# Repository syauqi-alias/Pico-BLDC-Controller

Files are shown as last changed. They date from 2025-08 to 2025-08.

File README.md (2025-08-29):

# Pico-BLDC-Controller



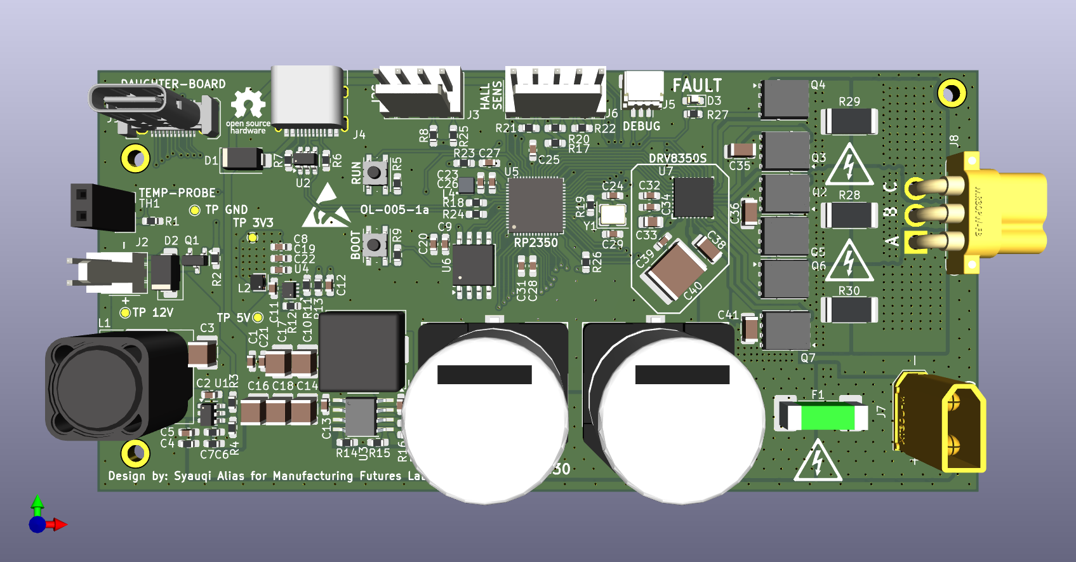
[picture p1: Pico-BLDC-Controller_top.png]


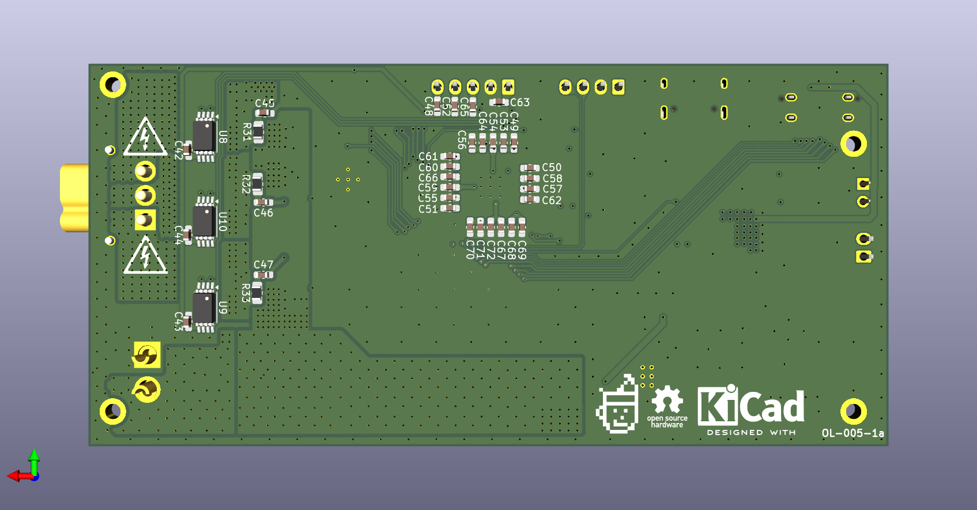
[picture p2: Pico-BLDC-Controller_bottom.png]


This project documents the design of a custom Brushless DC (BLDC) motor controller for a hotplate magnetic stirrer, intended for integration with an Opentrons automated liquid handling robot at the Manufacturing Future Lab, University College London.

---

## Project Overview

The primary goal is to create an open-source, accessible, and robust controller for a **260W 30V/7A Maxon BLDC motor**. This is my first venture into designing a motor controller, especially one involving a three-phase half-bridge topology. The journey is as much about learning as it is about the final product.

---

## Hardware Design

The schematic design is functionally complete and is currently undergoing peer review. The component selection process prioritized simplicity and a reduced component count to make the design easier to understand and replicate.

### Key Components:

* **Microcontroller:** **Raspberry Pi RP2350**
    * Chosen for its straightforward development environment and strong community support. While the ADC conversion speed can be a limitation for high-performance Field-Oriented Control (FOC), the goal is to create a baseline design that the open-source community can build upon and optimize.

* **Pre-driver:** **Texas Instruments DRV8350S**
    * This integrated gate driver significantly simplifies the design by handling much of the complexity associated with driving MOSFETs, such as the need for external charge pumps or bootstrap components. It reduces the overall component count and circuit complexity.

* **Motor:** **Maxon EC 90 flat Ø90 mm, brushless, 260 W, with Hall sensors**
    * A powerful 260W brushless motor, providing more than enough torque for stirring viscous solutions.

---

## Software and Firmware

The initial firmware will be developed using the **[simpleFOC](https://simplefoc.com/)** library to accelerate development and establish a functional baseline.

Once the hardware is validated, a longer-term goal is to develop custom firmware from scratch to fully optimize the controller's performance for this specific application.

---

## Current Status

**Status:** In Development (Last Updated: 29/08/2025)

* [x] Component selection finalized.
* [x] Initial schematic design complete.
* [x] Schematic peer review in progress.
* [x] PCB layout design.
* [X] PCB peer review 
* [X] Send out PCB to manufacturer
* [ ] Prototyping and hardware testing.
* [ ] Firmware development.

I'm actively seeking feedback on the schematic from colleagues and online forums. The design has evolved significantly through this iterative process, and I'll continue to post updates as the project progresses.

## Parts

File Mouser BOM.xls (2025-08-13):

Mfr Part Number (Input) | Manufacturer Part Number | Mouser Part Number | Manufacturer Name | Description | Quantity 1 | Unit Price 1 | Quantity 2 | Unit Price 2 | Quantity 3 | Unit Price 3 | Quantity 4 | Unit Price 4 | Quantity 5 | Unit Price 5 | Order Quantity | Order Unit Price | Min./Mult. | Availability | Lead Time in Days | Lifecycle | NCNR | RoHS | Pb Free | Package Type | Datasheet URL | Product Image | Design Risk
C0603C104K5RACAUTO |  | 80-C0603C104K5RAUTO |  | 100nF | 19
GRM32ER61C476KE15L |  | 81-GRM32ER61C476KE5L |  | 47uF | 3
GRM188D72A105KE01J |  | 81-GRM188D72A105KE1J |  | 1uF | 3
HMK107B7104KAHT |  | 963-HMK107B7104KAHT |  | 0.1uF 100V | 3
KGM15BR50J475KT,MCASL168BD7475KTCA01 |  |  |  | 4.7uF | 6
KGM15ACG1H121JT |  |  |  | 120pF | 1
HMK325B7225KN-T |  |  |  | 2.2uF | 2
KAM32LR72A475KU |  |  |  | 4.7uF | 1
GRM188R60J226MEA0D |  |  |  | 22uF | 2
0603YC101KAT2A,C0402C101K3RACAUTO |  |  |  | 100pF | 12
06033A150JAT2A |  |  |  | 15p | 2
EEV-FK2A331M |  |  |  | 330uF 100V | 2
GXT188R71C105KE13D |  |  |  | 1uF 16V | 2
C2012X7R2A473K125AA |  |  |  | 0.047uF | 1
CL31B105KCHNNNE |  |  |  | 1uF 100V | 4
CGA9N3X7S2A106K230KE |  |  |  | 10uF 100V | 1
 |  |  |  | C | 3
06033A100KAT2A |  |  |  | 10pF | 3
GCM188R71H103KA37J |  |  |  | 0.01uF | 2
SS12 |  |  |  | SS12 | 1
SS14 |  |  |  | SS14 | 1
 |  |  |  | LED | 1
0463030.ER |  |  |  | Fuse | 1
 |  |  |  | MountingHole | 4
 |  |  |  | Conn_01x10 | 1
217796-1021 |  |  |  | Heat Mat | 1
2042-11-22 |  |  |  | I2C CONN | 1
TYPE-C-31-M-12 |  |  |  | USB_C_Receptacle_USB2.0_14P | 1
SM03B-SRSS-TB(LF)(SN) |  |  |  | SM03B-SRSS-TB | 1
22-11-2052 |  |  |  | Conn_01x05 | 1
XT30U-M |  |  |  | Conn_01x02 | 1
MR30PW-F20.G.Y |  |  |  | Conn_01x03 | 1
MSS1210-153MED |  |  |  | 15uH | 1
74479275147 |  |  |  | 470nH | 1
MSS1038-153MLB |  |  |  | 15uH | 1
AOTA-B201610S3R3-101-T |  |  |  | 3.3uH | 1
DMN3053L-7 |  |  |  | DMN3053L-7 | 1
SIR680LDP |  |  |  | SIR680LDP | 6
AC0603JR-7W10KL,CRCW060310K0FKEI |  |  |  | 10k | 4
ERJ-3EKF4223V |  |  |  | 422k | 1
CRCW060322K1FKEBC |  |  |  | 22.1k | 1
RC0603FR-101KL |  |  |  | 1k | 7
CR0603-FX-5101ELF |  |  |  | 5.1k | 2
RC0603FR-7W4K7L |  |  |  | 4.7k | 2
CRCW0603100KFKEA |  |  |  | 100k | 2
ERJ-PB3B1003V |  |  |  | 100k | 1
CR0603-FX-4533ELF |  |  |  | 453k | 1
CRCW060364K9FKEA |  |  |  | 64.9k | 1
CR0603-FX-4022ELF |  |  |  | 40.2k | 1
CR0603-JW-270ELF |  |  |  | 27 | 2
AC0603DR-0733RL |  |  |  | 33 | 1
CRCW0603330RFKEC |  |  |  | 330 | 1
WSLP25122L000FEA |  |  |  | 2m | 3
 |  |  |  | R | 3
434133025816 |  |  |  | SW_Push | 2
B57560G1104F000 |  |  |  | 100k 200 C | 1
 |  |  |  | TestPoint | 4
LMR51430YFDDCR |  |  |  | LMR51430 | 1
82400102 |  |  |  | WE-TVS-82400102 | 1
LMR38020SDDAR |  |  |  | LMR38020SDDAR | 1
TPS62822DLCR |  |  |  | TPS62822DLC | 1
SC1509(13) |  |  |  | RP2350_60QFN | 1
W25Q128JVSIM TR |  |  |  | W25Q128JVS | 1
DRV8350SRTVT |  |  |  | DRV8350S | 1
INA240A2PWR |  |  |  | INA240A2PW | 3
ABM8-272-T3 |  |  |  | ABM8-272-T3 | 1

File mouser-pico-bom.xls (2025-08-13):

Mfr Part Number (Input) | Manufacturer Part Number | Mouser Part Number | Manufacturer Name | Description | Quantity 1 | Unit Price 1 | Quantity 2 | Unit Price 2 | Quantity 3 | Unit Price 3 | Quantity 4 | Unit Price 4 | Quantity 5 | Unit Price 5 | Order Quantity | Order Unit Price | Min./Mult. | Availability | Lead Time in Days | Lifecycle | NCNR | RoHS | Pb Free | Package Type | Datasheet URL | Product Image | Design Risk
80-C0603C104K5RAUTO |  |  |  |  | 19
81-GRM32ER61C476KE5L |  |  |  |  | 3
81-GRM188D72A105KE1J |  |  |  |  | 3
963-HMK107B7104KAHT |  |  |  |  | 3
963-MCASL168BD7475KT |  |  |  |  | 5
581-KGM15ACG1H121JT |  |  |  |  | 1
963-HMK325B7225KN-T |  |  |  |  | 2
581-KAM32LR72A475KU |  |  |  |  | 1
81-GRM188R60J226ME0D |  |  |  |  | 2
581-0603YC101KAT2A |  |  |  |  | 11
581-0603YC101KAT2A |  |  |  |  | 1
581-06033A150JAT2A |  |  |  |  | 2
667-EEV-FK2A331M |  |  |  |  | 2
81-GXT188R71C105KE3D |  |  |  |  | 2
810-C2012X7R2A473K |  |  |  |  | 1
187-CL31B105KCHNNNE |  |  |  |  | 4
810-CGA9N3X7S2A106KS |  |  |  |  | 1
581-06033A100K |  |  |  |  | 3
581-KGM15BR50J475KT |  |  |  |  | 1
81-GCM188R71H103KA7J |  |  |  |  | 2
821-SS12 |  |  |  |  | 1
821-SS14 |  |  |  |  | 1
720-LSQ976.01-N1Q2-1 |  |  |  |  | 1
576-0463030.ER |  |  |  |  | 1
306-B10BPHDSSLFSNP |  |  |  |  | 1
538-217796-1021 |  |  |  |  | 1
538-22-11-2042 |  |  |  |  | 1
306-SM03BSRSSTBLFSNP |  |  |  |  | 1
538-22-11-2052 |  |  |  |  | 1
994-MSS1210-153MED |  |  |  |  | 1
710-74479275147 |  |  |  |  | 1
994-MSS1038-153MLC |  |  |  |  | 1
815-AB201610S3R3101T |  |  |  |  | 1
637-MMFTN3402 |  |  |  |  | 1
78-SIR680LDP-T1-RE3 |  |  |  |  | 6
603-AC0603JR-7W10KL |  |  |  |  | 3
667-ERJ-3EKF4223V |  |  |  |  | 1
71-CRCW060322K1FKEBC |  |  |  |  | 1
603-RC0603FR-101KL |  |  |  |  | 7
652-CR0603FX-5101ELF |  |  |  |  | 2
603-RC0603FR-7W4K7L |  |  |  |  | 2
71-CRCW0603-100K-E3 |  |  |  |  | 2
667-ERJ-PB3B1003V |  |  |  |  | 1
652-CR0603FX-4533ELF |  |  |  |  | 1
71-CRCW0603-64.9K-E3 |  |  |  |  | 1
71-CRCW060310K0FKEI |  |  |  |  | 1
652-CR0603FX-4022ELF |  |  |  |  | 1
652-CR0603-JW-270ELF |  |  |  |  | 2
603-AC0603DR-0733RL |  |  |  |  | 1
71-CRCW0603330RFKEC |  |  |  |  | 1
71-WSLP25122L000FEA |  |  |  |  | 3
710-434133025816 |  |  |  |  | 2
871-B57560G1104F000 |  |  |  |  | 1
595-LMR51430YFDDCR |  |  |  |  | 1
710-82400102 |  |  |  |  | 1
595-LMR38020SDDAR |  |  |  |  | 1
595-TPS62822DLCR |  |  |  |  | 1
358-SC150913 |  |  |  |  | 1
454-W25Q128JVSIMTR |  |  |  |  | 1
595-DRV8350SRTVT |  |  |  |  | 1
595-INA240A2PWR |  |  |  |  | 3
815-ABM8-272-T3 |  |  |  |  | 1

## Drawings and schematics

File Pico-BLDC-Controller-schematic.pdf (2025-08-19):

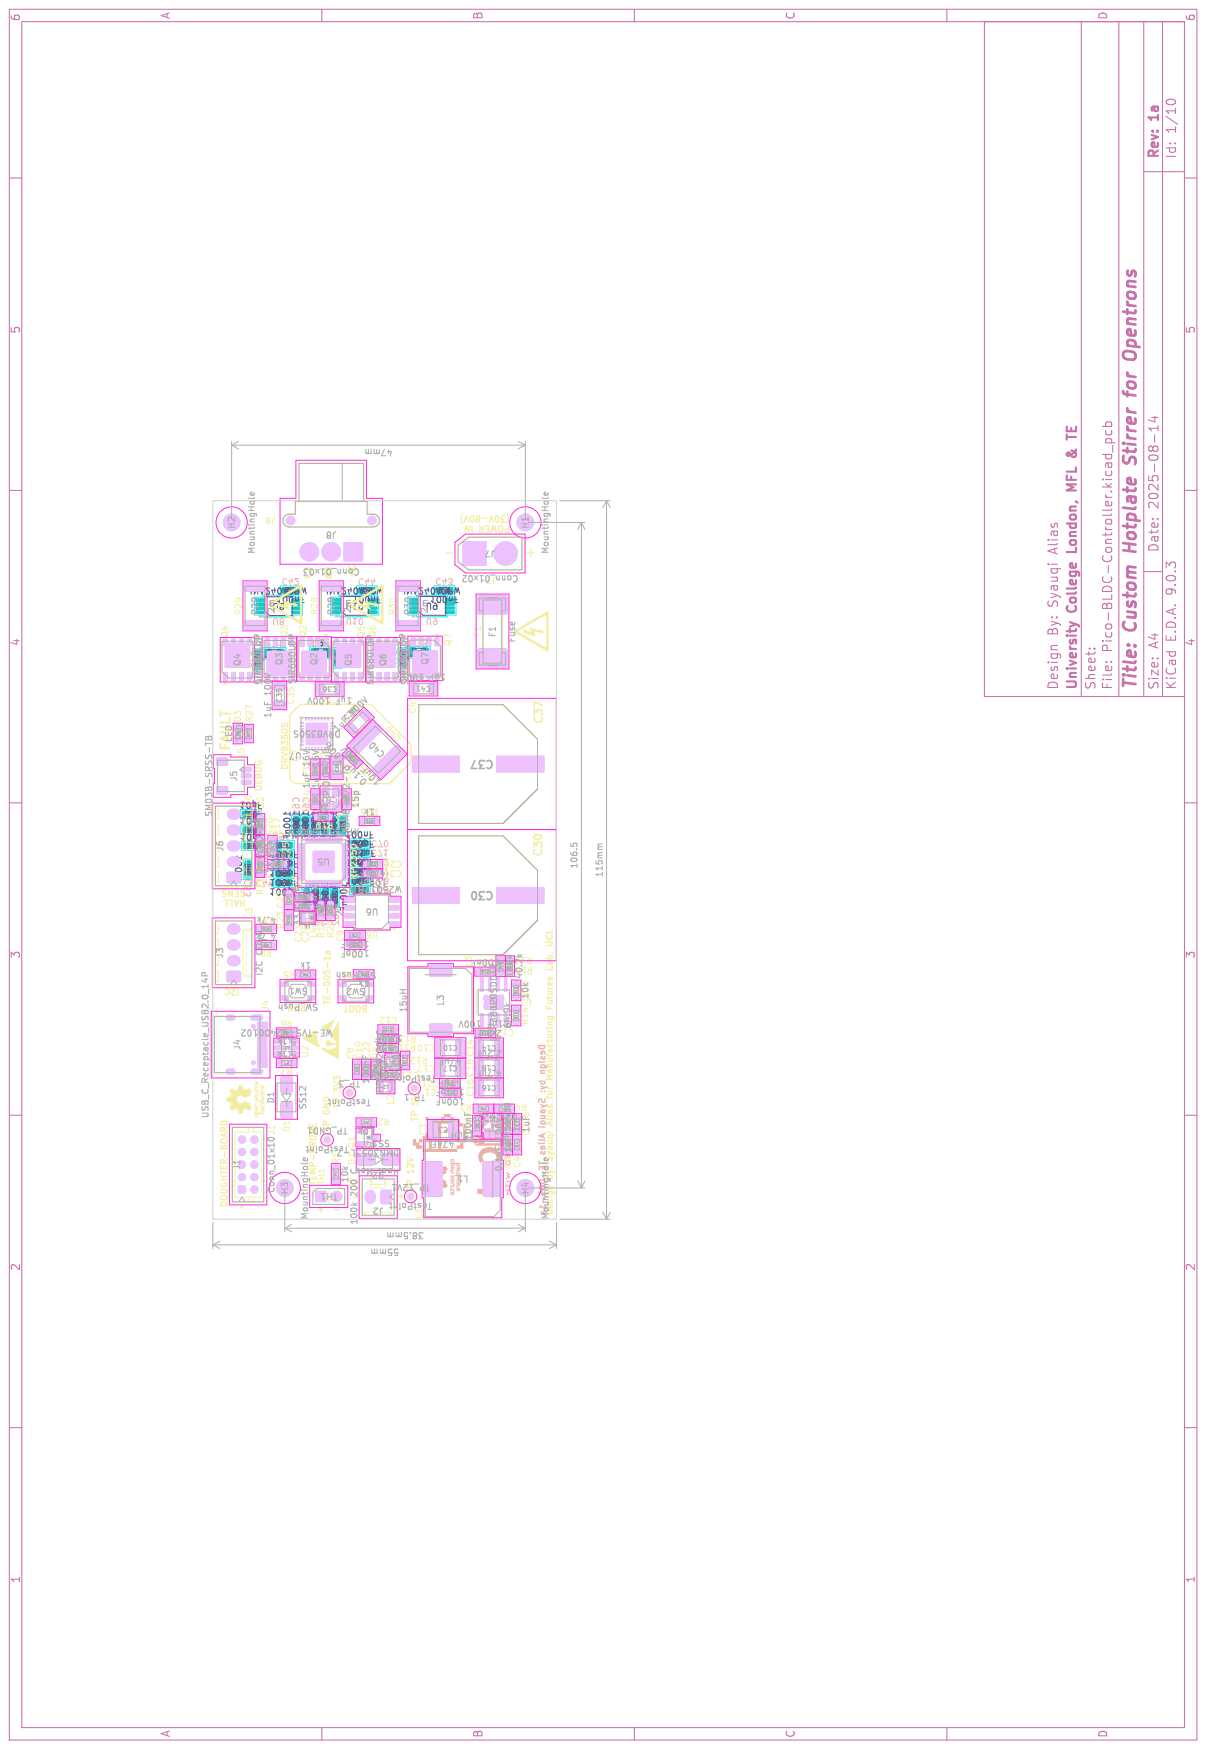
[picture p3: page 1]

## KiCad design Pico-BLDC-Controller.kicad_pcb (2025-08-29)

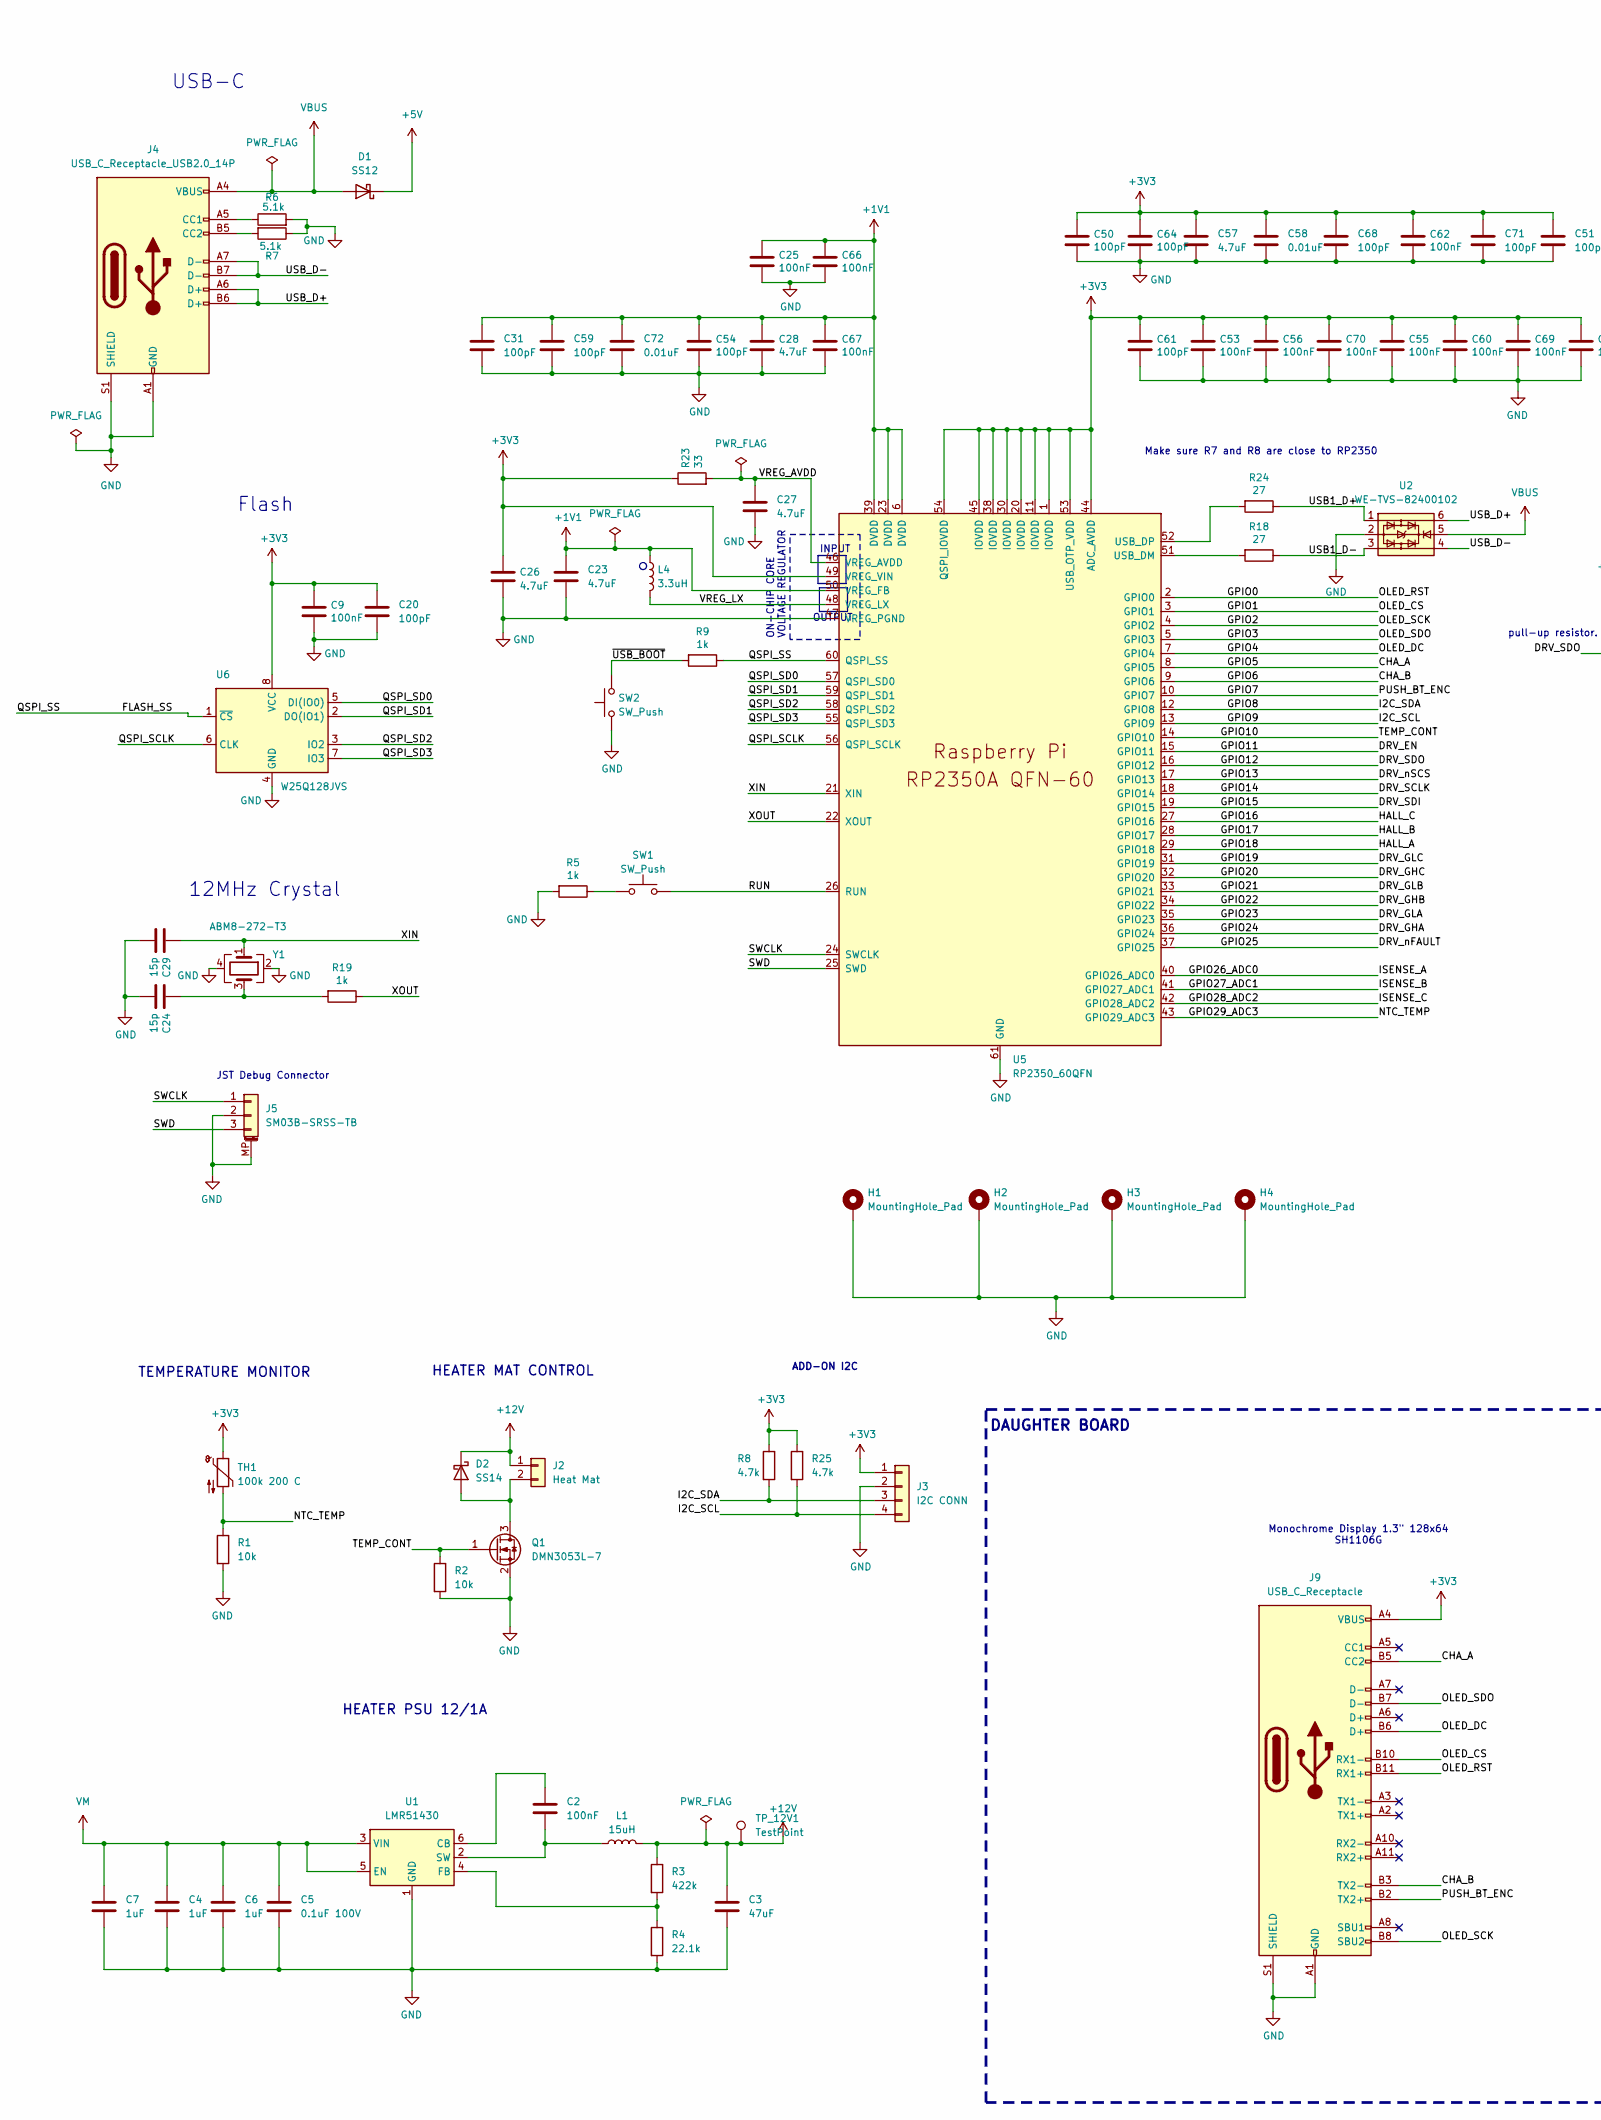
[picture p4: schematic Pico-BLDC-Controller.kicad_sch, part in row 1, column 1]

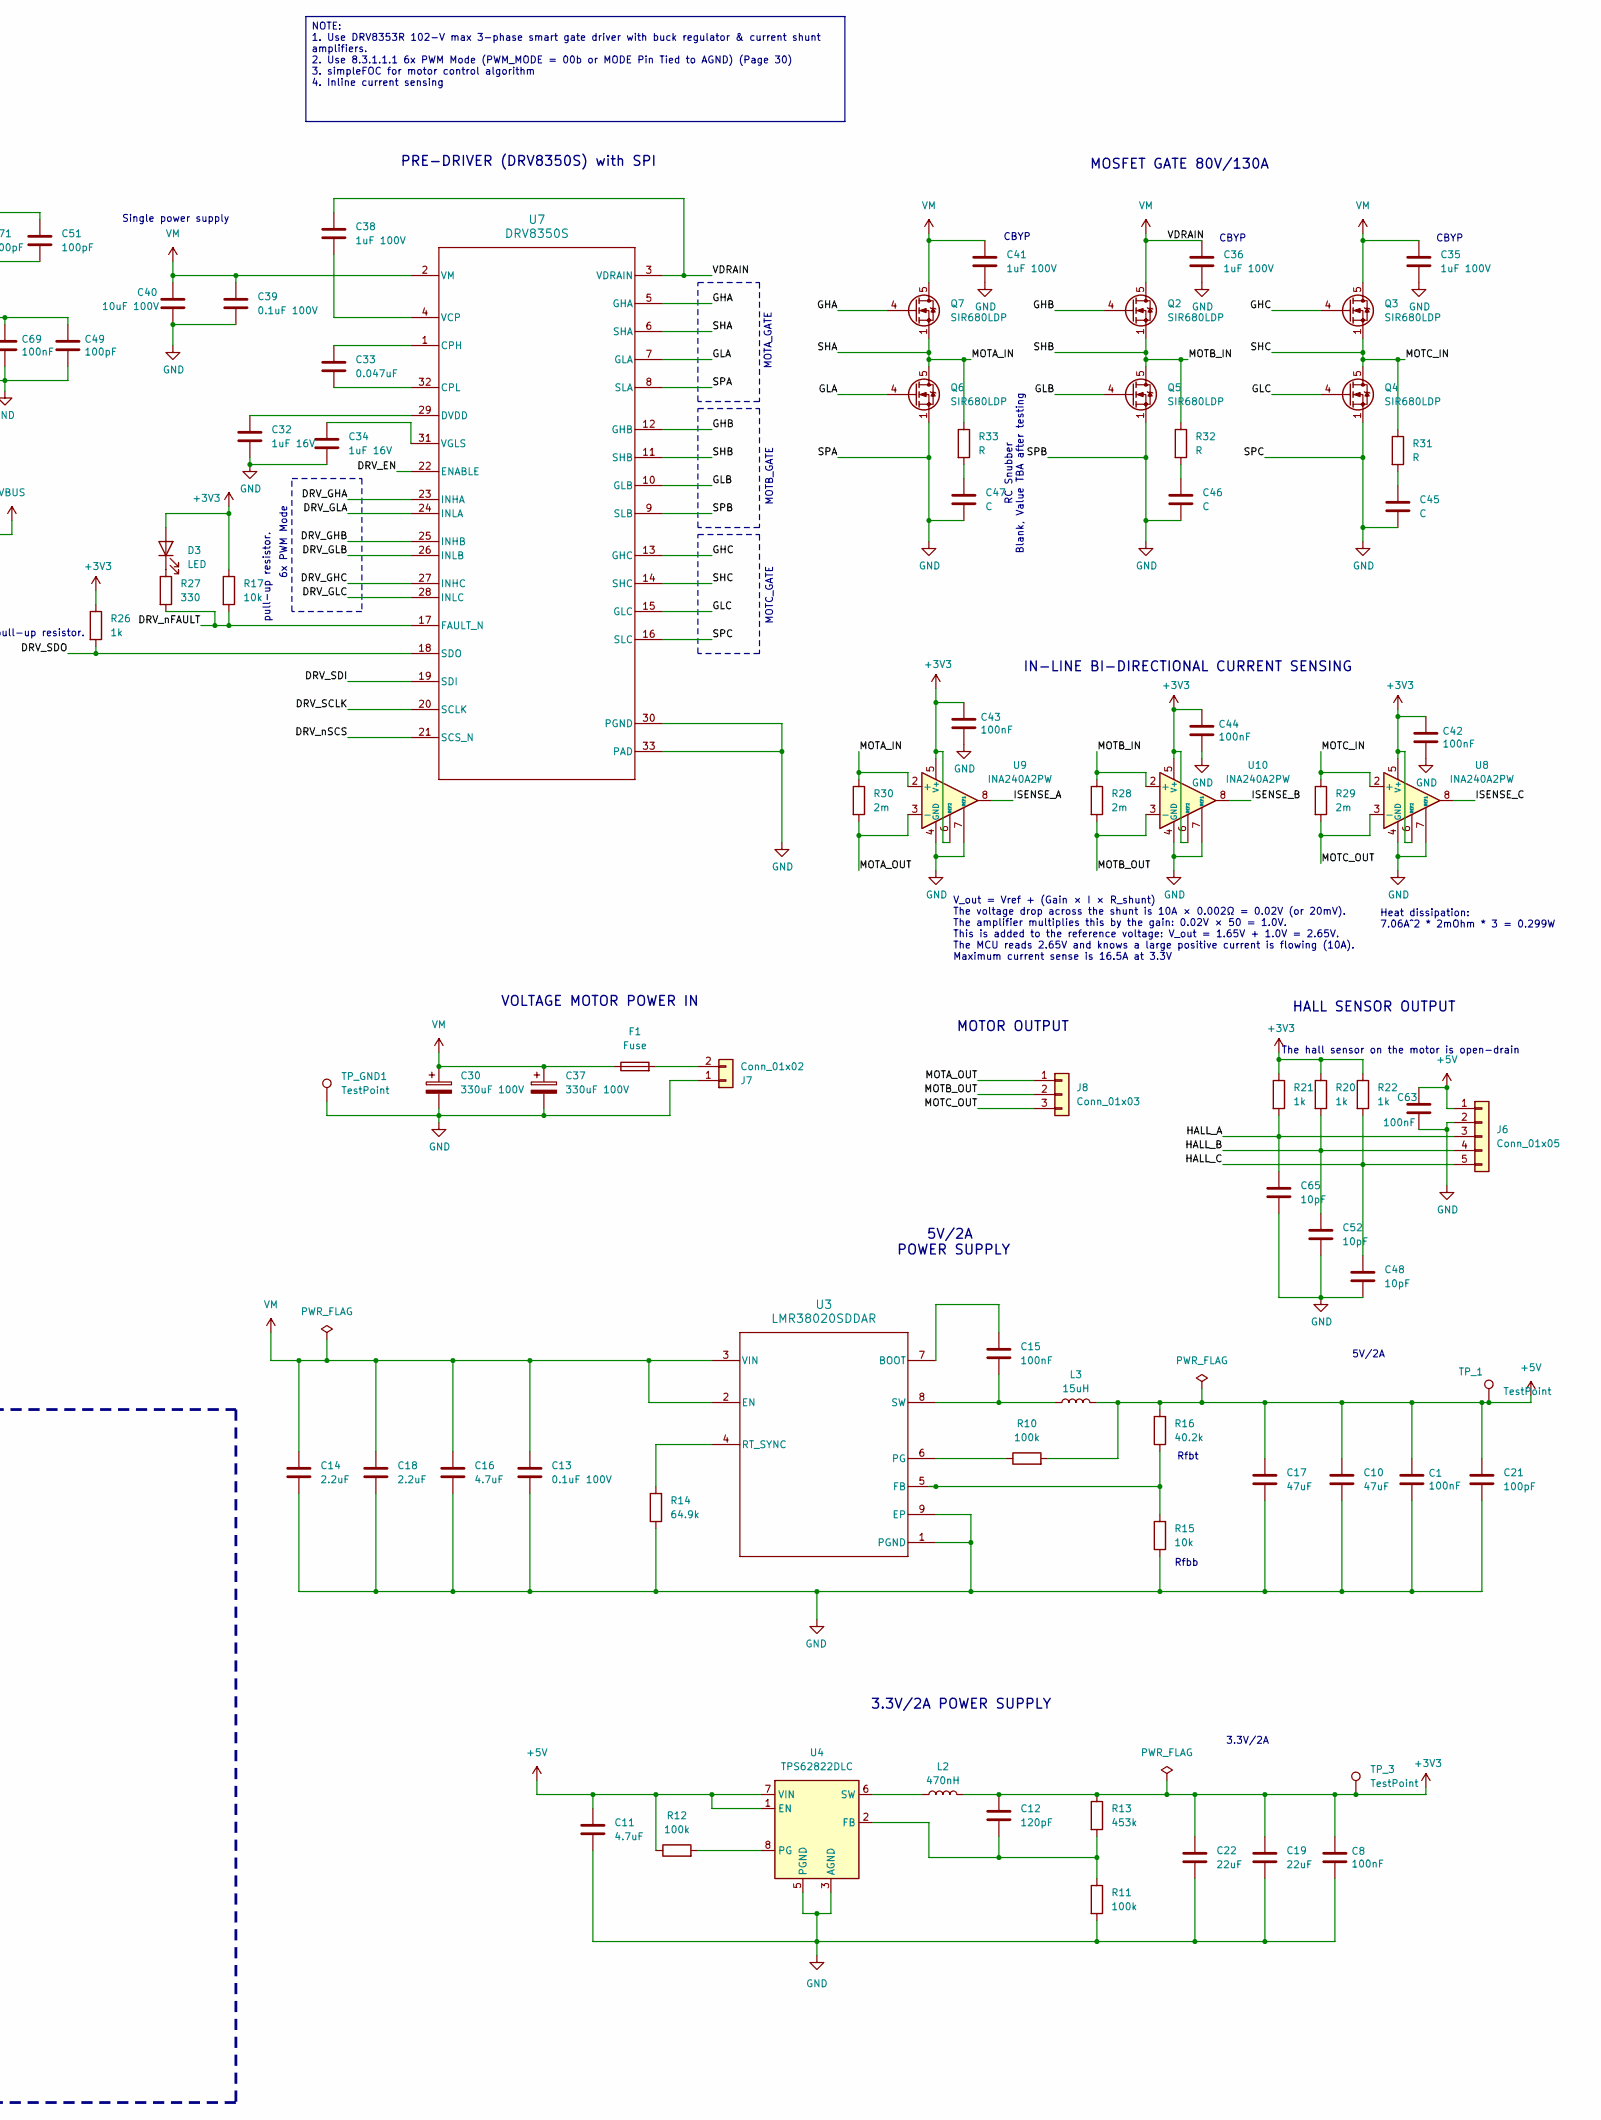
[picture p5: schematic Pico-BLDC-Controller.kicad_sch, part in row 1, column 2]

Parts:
C1, C2, C8, C9, C15, C25, C42, C43, C44, C53, C55, C56, C60, C62, C63, C66, C67, C69, C70: 100nF; C_0603_1608Metric_Pad1.08x0.95mm_HandSolder; MPN C0603C104K5RACAUTO
C3, C10, C17: 47uF; C_1210_3225Metric_Pad1.33x2.70mm_HandSolder; MPN GRM32ER61C476KE15L
C4, C6, C7: 1uF; R_0603_1608Metric_Pad0.98x0.95mm_HandSolder; MPN GRM188D72A105KE01J
C5, C13, C39: 0.1uF 100V; C_0603_1608Metric_Pad1.08x0.95mm_HandSolder; MPN HMK107B7104KAHT
C11, C23, C26, C27, C28: 4.7uF; C_0603_1608Metric_Pad1.08x0.95mm_HandSolder; MPN MCASL168BD7475KTCA01
C12: 120pF; C_0603_1608Metric_Pad1.08x0.95mm_HandSolder; MPN KGM15ACG1H121JT
C14, C18: 2.2uF; C_1210_3225Metric; MPN HMK325B7225KN-T
C16: 4.7uF; C_1210_3225Metric; MPN KAM32LR72A475KU
C19, C22: 22uF; C_0603_1608Metric_Pad1.08x0.95mm_HandSolder; MPN GRM188R60J226MEA0D
C20, C31, C49, C50, C51, C54, C59, C61, C64, C68, C71: 100pF; C_0603_1608Metric_Pad1.08x0.95mm_HandSolder; MPN 0603YC101KAT2A
C21: 100pF; C_0603_1608Metric_Pad1.08x0.95mm_HandSolder; MPN C0402C101K3RACAUTO
C24, C29: 15p; C_0603_1608Metric_Pad1.08x0.95mm_HandSolder; MPN 06033A150JAT2A
C30, C37: 330uF 100V; EEEFK0J103SM; MPN EEV-FK2A331M
C32, C34: 1uF 16V; C_0603_1608Metric_Pad1.08x0.95mm_HandSolder; MPN GXT188R71C105KE13D
C33: 0.047uF; C_0805_2012Metric_Pad1.18x1.45mm_HandSolder; MPN C2012X7R2A473K125AA
C35, C36, C38, C41: 1uF 100V; C_1206_3216Metric; MPN CL31B105KCHNNNE
C40: 10uF 100V; C_2220_5750Metric_Pad1.97x5.40mm_HandSolder; MPN CGA9N3X7S2A106K230KE
C45, C46, C47: C; C_0603_1608Metric_Pad1.08x0.95mm_HandSolder
C48, C52, C65: 10pF; C_0603_1608Metric_Pad1.08x0.95mm_HandSolder; MPN 06033A100KAT2A
C57: 4.7uF; C_0603_1608Metric_Pad1.08x0.95mm_HandSolder; MPN KGM15BR50J475KT
C58, C72: 0.01uF; C_0603_1608Metric_Pad1.08x0.95mm_HandSolder; MPN GCM188R71H103KA37J
D1: SS12; D_SMA; MPN SS12
D2: SS14; D_SMA; MPN SS14
D3: LED; LED_0603_1608Metric_Pad1.05x0.95mm_HandSolder
F1: Fuse; Fuse_Schurter_UMZ250; MPN 0463030.ER
H1, H2, H3, H4: MountingHole_Pad; MountingHole_2.2mm_M2_DIN965_Pad_TopBottom
J2: Heat Mat; Molex_KK-254_AE-6410-02A_1x02_P2.54mm_Vertical; MPN 217796-1021
J3: I2C CONN; Molex_KK-254_AE-6410-04A_1x04_P2.54mm_Vertical; MPN 22-11-2042
J4: USB_C_Receptacle_USB2.0_14P; USB_C_Receptacle_HRO_TYPE-C-31-M-12; MPN TYPE-C-31-M-12
J5: SM03B-SRSS-TB; JST_SH_SM03B-SRSS-TB_1x03-1MP_P1.00mm_Horizontal; MPN SM03B-SRSS-TB(LF)(SN)
J6: Conn_01x05; Molex_KK-254_AE-6410-05A_1x05_P2.54mm_Vertical; MPN 22-11-2052
J7: Conn_01x02; AMASS_XT30U-M_1x02_P5.0mm_Vertical; MPN XT30U-M
J8: Conn_01x03; AMASS_MR30PW-FB_1x03_P3.50mm_Horizontal; MPN MR30PW-F20.G.Y
J9: USB_C_Receptacle; USB_C_Receptacle_JAE_DX07S024WJ3R400
L1: 15uH; L_Coilcraft_MSS1210-XXX; MPN MSS1210-153MED
L2: 470nH; L_Wurth_WE-LQSH-2010; MPN 74479275147
L3: 15uH; L_Coilcraft_MSS1038-XXX; MPN MSS1038-153MLB
L4: 3.3uH; L_pol_2016; MPN AOTA-B201610S3R3-101-T
Q1: DMN3053L-7; SOT-23; MPN DMN3053L-7
Q2, Q3, Q4, Q5, Q6, Q7: SIR680LDP; PowerPAK_SO-8_Single; MPN SIR680LDP
R1, R2, R17: 10k; R_0603_1608Metric_Pad0.98x0.95mm_HandSolder; MPN AC0603JR-7W10KL
R3: 422k; R_0603_1608Metric_Pad0.98x0.95mm_HandSolder; MPN ERJ-3EKF4223V
R4: 22.1k; R_0603_1608Metric_Pad0.98x0.95mm_HandSolder; MPN CRCW060322K1FKEBC
R5, R9, R19, R20, R21, R22, R26: 1k; R_0603_1608Metric_Pad0.98x0.95mm_HandSolder; MPN RC0603FR-101KL
R6, R7: 5.1k; R_0603_1608Metric_Pad0.98x0.95mm_HandSolder; MPN CR0603-FX-5101ELF
R8, R25: 4.7k; R_0603_1608Metric_Pad0.98x0.95mm_HandSolder; MPN RC0603FR-7W4K7L
R10, R11: 100k; R_0603_1608Metric_Pad0.98x0.95mm_HandSolder; MPN CRCW0603100KFKEA
R12: 100k; R_0603_1608Metric; MPN ERJ-PB3B1003V
R13: 453k; R_0603_1608Metric_Pad0.98x0.95mm_HandSolder; MPN CR0603-FX-4533ELF
R14: 64.9k; R_0603_1608Metric_Pad0.98x0.95mm_HandSolder; MPN CRCW060364K9FKEA
R15: 10k; R_0603_1608Metric_Pad0.98x0.95mm_HandSolder; MPN CRCW060310K0FKEI
R16: 40.2k; R_0603_1608Metric_Pad0.98x0.95mm_HandSolder; MPN CR0603-FX-4022ELF
R18, R24: 27; R_0603_1608Metric_Pad0.98x0.95mm_HandSolder; MPN CR0603-JW-270ELF
R23: 33; R_0603_1608Metric_Pad0.98x0.95mm_HandSolder; MPN AC0603DR-0733RL
R27: 330; R_0603_1608Metric; MPN CRCW0603330RFKEC
R28, R29, R30: 2m; R_2512_6332Metric_Pad1.40x3.35mm_HandSolder; MPN WSLP25122L000FEA
R31, R32, R33: R; R_0805_2012Metric_Pad1.20x1.40mm_HandSolder
SW1, SW2: SW_Push; SW_Push_1P1T_NO_Vertical_Wuerth_434133025816; MPN 434133025816
TH1: 100k 200 C; PinSocket_1x02_P2.54mm_Vertical; MPN B57560G1104F000
TP_1, TP_3, TP_12V1: TestPoint; TestPoint_Pad_D1.0mm
TP_GND1: TestPoint; TestPoint_Pad_D1.0mm
U1: LMR51430; SOT-23-6; MPN LMR51430YFDDCR
U2: WE-TVS-82400102; SOT-23-6; MPN 82400102
U3: LMR38020SDDAR; DDA0008E-MFG; MPN LMR38020SDDAR
U4: TPS62822DLC; Texas_VSON-HR-8_1.5x2mm_P0.5mm; MPN TPS62822DLCR
U5: RP2350_60QFN; RP2350-QFN-60-1EP_7x7_P0.4mm_EP3.4x3.4mm_ThermalVias; MPN SC1509(13)
U6: W25Q128JVS; SOIC-8_5.3x5.3mm_P1.27mm; MPN W25Q128JVSIM TR
U7: DRV8350S; RTV0032E; MPN DRV8350SRTVT
U8, U9, U10: INA240A2PW; TSSOP-8_4.4x3mm_P0.65mm; MPN INA240A2PWR
Y1: ABM8-272-T3; Crystal_SMD_3225-4Pin_3.2x2.5mm; MPN ABM8-272-T3

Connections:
+1V1: C23.1, C25.1, C28.1, C31.1, C54.1, C59.1, C66.1, C67.1, C72.1, L4.1, U5.6 (DVDD), U5.23 (DVDD), U5.39 (DVDD), U5.50 (VREG_FB)
+3V3: C8.1, C9.1, C12.1, C19.1, C20.1, C22.1, C26.1, C42.1, C43.1, C44.1, C49.1, C50.1, C51.1, C53.1, C55.1, C56.1, C57.1, C58.1, C60.1, C61.1, C62.1, C64.1, C68.1, C69.1, C70.1, C71.1, D3.2 (A), J3.1, J9.A4 (VBUS), J9.A9 (VBUS), J9.B4 (VBUS), J9.B9 (VBUS), L2.2, R8.1, R13.1, R17.1, R20.1, R21.1, R22.1, R23.1, R25.1, R26.1, TH1.1, TP_3.1, U5.1 (IOVDD), U5.11 (IOVDD), U5.20 (IOVDD), U5.30 (IOVDD), U5.38 (IOVDD), U5.44 (ADC_AVDD), U5.45 (IOVDD), U5.49 (VREG_VIN), U5.53 (USB_OTP_VDD), U5.54 (QSPI_IOVDD), U6.8 (VCC), U8.5 (V+), U8.6 (REF2), U9.5 (V+), U9.6 (REF2), U10.5 (V+), U10.6 (REF2)
+5V: C1.1, C10.1, C11.1, C17.1, C21.1, C63.1, D1.1 (K), J6.1, L3.2, R10.2, R12.1, R16.2, TP_1.1, U4.1 (EN), U4.7 (VIN)
+12V: C3.1, D2.1 (K), J2.1, L1.2, R3.1, TP_12V1.1
/CHA_A: J9.B5 (CC2), U5.8 (GPIO5)
/CHA_B: J9.B3 (TX2-), U5.9 (GPIO6)
/DRV_EN: U5.15 (GPIO11), U7.22 (ENABLE)
/DRV_GHA: U5.36 (GPIO24), U7.23 (INHA)
/DRV_GHB: U5.34 (GPIO22), U7.25 (INHB)
/DRV_GHC: U5.32 (GPIO20), U7.27 (INHC)
/DRV_GLA: U5.35 (GPIO23), U7.24 (INLA)
/DRV_GLB: U5.33 (GPIO21), U7.26 (INLB)
/DRV_GLC: U5.31 (GPIO19), U7.28 (INLC)
/DRV_SCLK: U5.18 (GPIO14), U7.20 (SCLK)
/DRV_SDI: U5.19 (GPIO15), U7.19 (SDI)
/DRV_SDO: R26.2, U5.16 (GPIO12), U7.18 (SDO)
/DRV_nFAULT: R17.2, R27.2, U5.37 (GPIO25), U7.17 (FAULT_N)
/DRV_nSCS: U5.17 (GPIO13), U7.21 (SCS_N)
/FLASH_SS: R9.1, U5.60 (QSPI_SS), U6.1 (~CS)
/GHA: Q7.4 (G), U7.5 (GHA)
/GHB: Q2.4 (G), U7.12 (GHB)
/GHC: Q3.4 (G), U7.13 (GHC)
/GLA: Q6.4 (G), U7.7 (GLA)
/GLB: Q5.4 (G), U7.10 (GLB)
/GLC: Q4.4 (G), U7.15 (GLC)
/GPIO0: J9.B11 (RX1+), U5.2 (GPIO0)
/GPIO1: J9.B10 (RX1-), U5.3 (GPIO1)
/GPIO2: J9.B8 (SBU2), U5.4 (GPIO2)
/GPIO3: J9.B7 (D-), U5.5 (GPIO3)
/GPIO4: J9.B6 (D+), U5.7 (GPIO4)
/GPIO7: J9.B2 (TX2+), U5.10 (GPIO7)
/GPIO8: J3.3, R8.2, U5.12 (GPIO8)
/GPIO9: J3.4, R25.2, U5.13 (GPIO9)
/GPIO10: Q1.1 (G), R2.1, U5.14 (GPIO10)
/GPIO16: C48.1, J6.5, R22.2, U5.27 (GPIO16)
/GPIO17: C52.1, J6.4, R20.2, U5.28 (GPIO17)
/GPIO18: C65.1, J6.3, R21.2, U5.29 (GPIO18)
/GPIO26_ADC0: U5.40 (GPIO26_ADC0), U9.8
/GPIO27_ADC1: U5.41 (GPIO27_ADC1), U10.8
/GPIO28_ADC2: U5.42 (GPIO28_ADC2), U8.8
/GPIO29_ADC3: R1.1, TH1.2, U5.43 (GPIO29_ADC3)
/MOTA_IN: Q6.5 (D), Q7.1 (S), Q7.2 (S), Q7.3 (S), R30.1, R33.1, U7.6 (SHA), U9.2 (+)
/MOTA_OUT: J8.1, R30.2, U9.3 (-)
/MOTB_IN: Q2.1 (S), Q2.2 (S), Q2.3 (S), Q5.5 (D), R28.1, R32.1, U7.11 (SHB), U10.2 (+)
/MOTB_OUT: J8.2, R28.2, U10.3 (-)
/MOTC_IN: Q3.1 (S), Q3.2 (S), Q3.3 (S), Q4.5 (D), R29.1, R31.1, U7.14 (SHC), U8.2 (+)
/MOTC_OUT: J8.3, R29.2, U8.3 (-)
/QSPI_SCLK: U5.56 (QSPI_SCLK), U6.6 (CLK)
/QSPI_SD0: U5.57 (QSPI_SD0), U6.5 (DI(IO0))
/QSPI_SD1: U5.59 (QSPI_SD1), U6.2 (DO(IO1))
/QSPI_SD2: U5.58 (QSPI_SD2), U6.3 (IO2)
/QSPI_SD3: U5.55 (QSPI_SD3), U6.7 (IO3)
/RUN: SW1.2, U5.26 (RUN)
/SWCLK: J5.1, U5.24 (SWCLK)
/SWD: J5.3, U5.25 (SWD)
/USB1_D+: R24.1, U2.1
/USB1_D-: R18.1, U2.3
/USB_D+: J4.A6 (D+), J4.B6 (D+), U2.6
/USB_D-: J4.A7 (D-), J4.B7 (D-), U2.4
/VREG_AVDD: C27.1, R23.2, U5.46 (VREG_AVDD)
/VREG_LX: L4.2, U5.48 (VREG_LX)
/XIN: C29.1, U5.21 (XIN), Y1.1
/XOUT: R19.1, U5.22 (XOUT)
/~USB_BOOT: R9.2, SW2.2
GND: C1.2, C3.2, C4.2, C5.2, C6.2, C7.2, C8.2, C9.2, C10.2, C11.2, C13.2, C14.2, C16.2, C17.2, C18.2, C19.2, C20.2, C21.2, C22.2, C23.2, C24.2, C25.2, C26.2, C27.2, C28.2, C29.2, C30.2, C31.2, C32.2, C34.2, C35.2, C36.2, C37.2, C39.2, C40.2, C41.2, C42.2, C43.2, C44.2, C45.2, C46.2, C47.2, C48.2, C49.2, C50.2, C51.2, C52.2, C53.2, C54.2, C55.2, C56.2, C57.2, C58.2, C59.2, C60.2, C61.2, C62.2, C63.2, C64.2, C65.2, C66.2, C67.2, C68.2, C69.2, C70.2, C71.2, C72.2, H1.1, H2.1, H3.1, H4.1, J3.2, J4.A1 (GND), J4.A12 (GND), J4.B1 (GND), J4.B12 (GND), J4.S1 (SHIELD), J5.2, J5.MP (MountPin), J6.2, J7.1, J9.A1 (GND), J9.A12 (GND), J9.B1 (GND), J9.B12 (GND), J9.S1 (SHIELD), Q1.2 (S), Q4.1 (S), Q4.2 (S), Q4.3 (S), Q5.1 (S), Q5.2 (S), Q5.3 (S), Q6.1 (S), Q6.2 (S), Q6.3 (S), R1.2, R2.2, R4.2, R5.2, R6.2, R7.1, R11.2, R14.1, R15.1, SW2.1, TP_GND1.1, U1.1 (GND), U2.2, U3.1 (PGND), U3.9 (EP), U3.10, U3.11, U3.12, U3.13, U3.14, U3.15, U4.3 (AGND), U4.5 (PGND), U5.47 (VREG_PGND), U5.61 (GND), U6.4 (GND), U7.8 (SLA), U7.9 (SLB), U7.16 (SLC), U7.30 (PGND), U7.33 (PAD), U8.1 (GND), U8.4 (GND), U8.7 (REF1), U9.1 (GND), U9.4 (GND), U9.7 (REF1), U10.1 (GND), U10.4 (GND), U10.7 (REF1), Y1.2, Y1.4
unnamed: C24.1, R19.2, Y1.3
unnamed: C45.1, R31.2
unnamed: C46.1, R32.2
unnamed: C47.1, R33.2
unnamed: D2.2 (A), J2.2, Q1.3 (D)
unnamed: D3.1 (K), R27.1
unnamed: J4.A5 (CC1), R6.1
unnamed: J4.B5 (CC2), R7.2
unnamed: F1.2, J7.2
unnamed: R5.1, SW1.1
unnamed: C2.1, U1.6 (CB)
unnamed: R3.2, R4.1, U1.4 (FB)
unnamed: C2.2, L1.1, U1.2 (SW)
unnamed: C15.1, U3.7 (BOOT)
unnamed: R15.2, R16.1, U3.5 (FB)
unnamed: R10.1, U3.6 (PG)
unnamed: R14.2, U3.4 (RT_SYNC)
unnamed: C15.2, L3.1, U3.8 (SW)
unnamed: C12.2, R11.1, R13.2, U4.2 (FB)
unnamed: R12.2, U4.8 (PG)
unnamed: L2.1, U4.6 (SW)
unnamed: R18.2, U5.51 (USB_DM)
unnamed: R24.2, U5.52 (USB_DP)
unnamed: C33.1, U7.1 (CPH)
unnamed: C33.2, U7.32 (CPL)
unnamed: C32.1, U7.29 (DVDD)
unnamed: C38.2, U7.4 (VCP)
unnamed: C34.1, U7.31 (VGLS)
VBUS: D1.2 (A), J4.A4 (VBUS), J4.A9 (VBUS), J4.B4 (VBUS), J4.B9 (VBUS), U2.5
VM: C4.1, C5.1, C6.1, C7.1, C13.1, C14.1, C16.1, C18.1, C30.1, C35.1, C36.1, C37.1, C38.1, C39.1, C40.1, C41.1, F1.1, Q2.5 (D), Q3.5 (D), Q7.5 (D), U1.3 (VIN), U1.5 (EN), U3.2 (EN), U3.3 (VIN), U7.2 (VM), U7.3 (VDRAIN)

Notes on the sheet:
CBYP
PRE-DRIVER (DRV8350S) with SPI
3.3V/2A POWER SUPPLY
TEMPERATURE MONITOR
3.3V/2A
Rfbt
Heat dissipation: 7.06A^2 * 2mOhm * 3 = 0.299W
12MHz Crystal
MOTC_GATE
INPUT
MOTOR OUTPUT
Rfbb
Monochrome Display 1.3" 128x64 SH1106G
pull-up resistor.
6x PWM Mode
5V/2A POWER SUPPLY
JST Debug Connector
IN-LINE BI-DIRECTIONAL CURRENT SENSING
HALL SENSOR OUTPUT
RC Snubber Blank, Value TBA after testing
Make sure R7 and R8 are close to RP2350
5V/2A
DAUGHTER BOARD
OUTPUT
HEATER MAT CONTROL
MOTA_GATE
MOSFET GATE 80V/130A
V_out = Vref + (Gain × I × R_shunt) The voltage drop across the shunt is 10A × 0.002Ω = 0.02V (or 20mV). The amplifier multiplies this by the gain: 0.02V × 50 = 1.0V. This is added to the reference voltage: V_out = 1.65V + 1.0V = 2.65V. The MCU reads 2.65V and knows a large positive current is flow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
VOLTAGE MOTOR POWER IN
ADD-ON I2C
USB-C
ON-CHIP CORE VOLTAGE REGULATOR
HEATER PSU 12/1A
Flash
Single power supply
The hall sensor on the motor is open-drain
MOTB_GATE
NOTE: 1. Use DRV8353R 102-V max 3-phase smart gate driver with buck regulator & current shunt amplifiers. 2. Use 8.3.1.1.1 6x PWM Mode (PWM_MODE = 00b or MODE Pin Tied to AGND) (Page 30) 3. simpleFOC for motor control algorithm 4. Inline current sensing

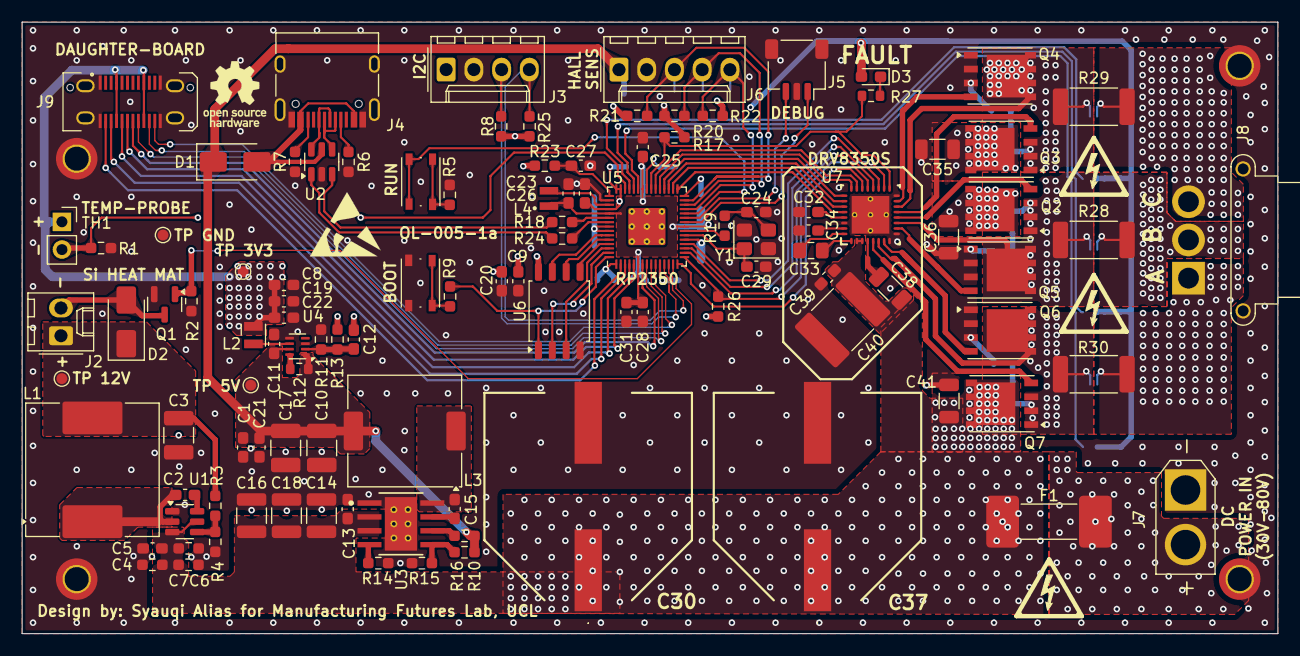
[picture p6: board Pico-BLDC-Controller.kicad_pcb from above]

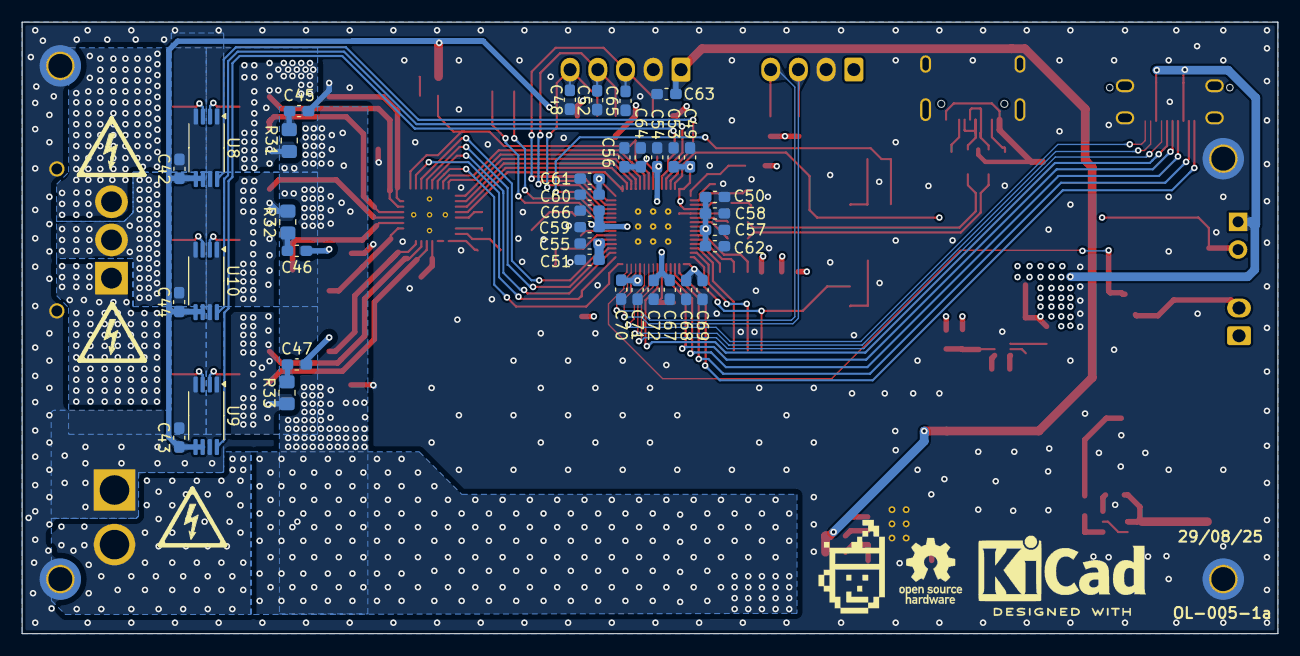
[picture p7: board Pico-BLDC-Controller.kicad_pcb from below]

Board: 4 copper layers, 115.0 x 56.0 mm, 150 parts (37 on the bottom side), 95 nets.

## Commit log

2025-07-29 Your commit message
    [Pico-BLDC-Controller.kicad_pcb, Pico-BLDC-Controller.kicad_sch]
2025-08-27 change connector to usb-c
    [Pico-BLDC-Controller.kicad_pcb, Pico-BLDC-Controller.kicad_sch]
2025-08-27 update silkscreen
    [Pico-BLDC-Controller.kicad_pcb]
2025-08-28 increase board size and more vias
    [Pico-BLDC-Controller.kicad_pcb]
2025-08-29 added date on silkscreen
    [Pico-BLDC-Controller.kicad_pcb]
